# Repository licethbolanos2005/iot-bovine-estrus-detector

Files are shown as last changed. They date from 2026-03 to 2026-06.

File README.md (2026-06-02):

# 🐄 IoT Bovine Estrus Detector

Prototipo IoT basado en tecnología **LoRa** para la detección temprana del celo en bovinos mediante el monitoreo continuo de variables fisiológicas y comportamentales.

> Proyecto integrador — Ingeniería Electrónica  
> Unidad Central del Valle del Cauca - Semestre 8
> Autores: Liceth Bolaños, Santiago Albarracin, Arlyn Cardozo, Samuel Guevara

---

## 📋 Descripción general

El sistema integra un nodo transmisor montado en un chaleco portador adaptado al animal, el cual captura temperatura corporal, actividad motora, frecuencia respiratoria y eventos de monta. Los datos son procesados por un **ESP32 LoRa V3 (ESP32-S3 + SX1262)**, almacenados localmente en MicroSD con marca temporal RTC y transmitidos de forma inalámbrica al nodo receptor, donde son visualizados en **Grafana** a través de **InfluxDB**.

---

## 📁 Estructura del repositorio

```
iot-bovine-estrus-detector/
│
├── Board/                  # Diseño final de la PCB (KiCad)
│   └── ...                 # Archivos .kicad_pcb, .kicad_sch, Gerbers
│
├── Box/                    # Diseño de la caja de protección (impresión 3D)
│   └── ...                 # Archivos .ipt
│
├── Receiver_Code/          # Firmware del nodo receptor
│   └── ...                 # Código ESP32 — recepción LoRa, envío a InfluxDB
│
├── Schematic/              # Esquemático electrónico del sistema
│   └── ...                 # Archivos .kicad_sch
│
├── Transmitter_Code/       # Firmware del nodo transmisor
│   └── ...                 # Código ESP32 — sensores, LoRa, MicroSD, RTC, Web server
│
└── README.md
```

---

## ⚙️ Hardware utilizado

| Componente | Función |
|---|---|
| WiFi LoRa 32 V3 (ESP32-S3 + SX1262) | Unidad central de procesamiento y comunicación |
| DS18B20 | Medición de temperatura corporal |
| MPU6050 | Actividad motora y frecuencia respiratoria |
| FSR (Force Sensitive Resistor) | Detección de eventos de monta |
| INA219 | Monitoreo de consumo energético |
| DS3231 (RTC) | Registro temporal de datos |
| Módulo MicroSD TF | Almacenamiento local de datos |
| Batería LiPo 3.7V | Alimentación del sistema |

---

## 📡 Parámetros de comunicación LoRa

| Parámetro | Valor |
|---|---|
| Banda | 915 MHz (ISM) |
| Spreading Factor | 7 |
| Bandwidth | 125 kHz |
| Coding Rate | 5 |
| Sync Word | 0x12 |
| Potencia TX | 14 dBm |

---

## 🖥️ Arquitectura del sistema

```
[Sensores] → [ESP32 Transmisor] → [LoRa 915 MHz] → [ESP32 Receptor]
                    ↓                                        ↓
               [MicroSD + RTC]                        [InfluxDB → Grafana]
                    ↓
             [Servidor Web Embebido / OTA]
```

---

## 🚀 Primeros pasos

### Requisitos

- [Arduino IDE](https://www.arduino.cc/en/software) o [PlatformIO](https://platformio.org/)
- Placa: **Heltec WiFi LoRa 32 V3**
- Librerías necesarias:
  - `RadioLib`
  - `OneWire` + `DallasTemperature`
  - `MPU6050`
  - `RTClib`
  - `SD`
  - `INA219`
  - `ArduinoJson`
  - `ESPAsyncWebServer`

### Cargar firmware transmisor

1. Abre `Transmitter_Code/` en Arduino IDE o PlatformIO.
2. Configura los parámetros de red WiFi y LoRa en el archivo de configuración.
3. Compila y carga en la placa ESP32 del nodo transmisor.

### Cargar firmware receptor

1. Abre `Receiver_Code/` en Arduino IDE o PlatformIO.
2. Configura la dirección IP de InfluxDB y las credenciales de red.
3. Compila y carga en la placa ESP32 del nodo receptor.

---

## 📊 Visualización

Los datos son enviados a **InfluxDB** y visualizados en tiempo real mediante **Grafana**, donde se monitorean:

- Temperatura corporal (°C)
- Magnitud de aceleración (actividad motora)
- Frecuencia respiratoria
- Consumo energético (mA)
- Estado de celo (algoritmo de detección)
- Eventos de monta (FSR)
- Calidad del enlace LoRa (RSSI / SNR)

---

## 🌐 Servidor web embebido

El nodo transmisor implementa un servidor web accesible en la red local mediante:

```
http://boviot.local
```

Desde la interfaz web es posible:
- Visualizar variables fisiológicas en tiempo real
- Configurar parámetros de red WiFi
- Actualizar el firmware de forma inalámbrica (**OTA**)

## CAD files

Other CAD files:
Box/Caja PI/OldVersions/base.0005.ipt
Box/Caja PI/base.ipt
Box/Caja PI/tapa.ipt

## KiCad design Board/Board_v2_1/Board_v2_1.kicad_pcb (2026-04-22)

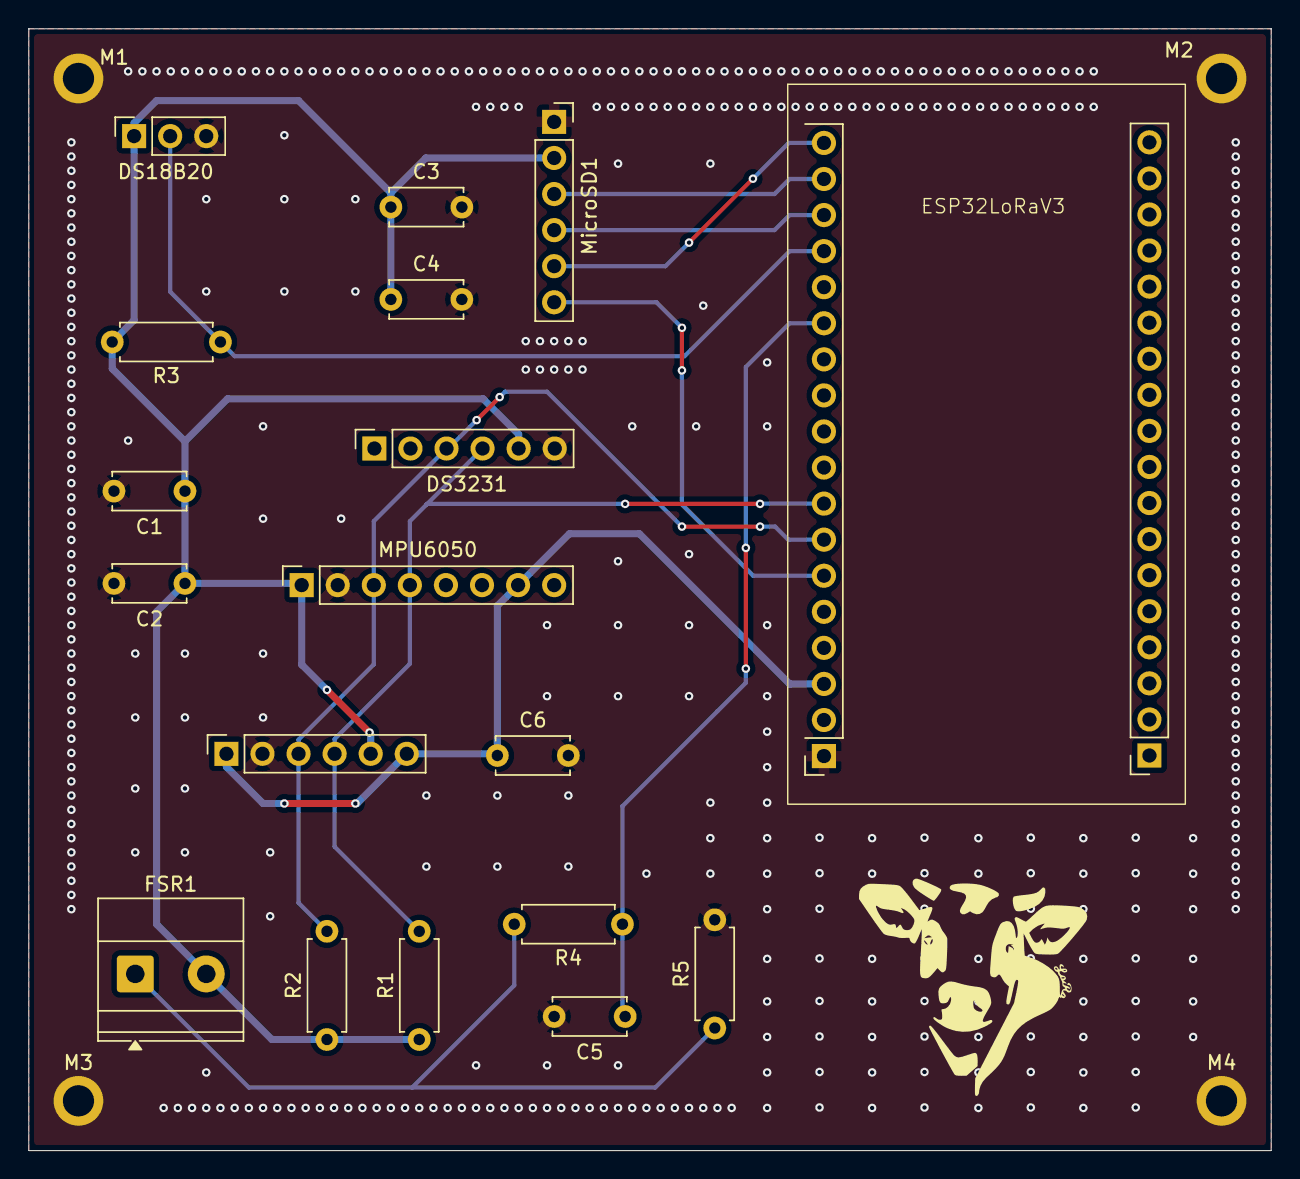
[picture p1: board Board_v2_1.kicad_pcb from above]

Board: 2 copper layers, 87.5 x 79.0 mm, 22 parts (0 on the bottom side), 12 nets.

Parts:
C1, C3, C5, C6: 100nf; C_Disc_D5.0mm_W2.5mm_P5.00mm
C2, C4: 10uf; C_Disc_D5.0mm_W2.5mm_P5.00mm
DS18B20: Conn_01x03; PinSocket_1x03_P2.54mm_Vertical
DS3231: PinSocket_1x06_P2.54mm_Vertical
ESP32LoRaV3: ESP32 Lora V3
FSR1: Conn_01x02; TerminalBlock_Phoenix_MKDS-1,5-2_1x02_P5.00mm_Horizontal
INA219: PinSocket_1x06_P2.54mm_Vertical
M1, M2, M3, M4: MountingHole_2.2mm_M2_ISO7380_Pad
MPU6050: Conn_01x08; PinSocket_1x08_P2.54mm_Vertical
MicroSD1: PinSocket_1x06_P2.54mm_Vertical
R1, R2, R3: 4.7K; R_Axial_DIN0207_L6.3mm_D2.5mm_P7.62mm_Horizontal
R4: 10K; R_Axial_DIN0207_L6.3mm_D2.5mm_P7.62mm_Horizontal
R5: 50K; R_Axial_DIN0207_L6.3mm_D2.5mm_P7.62mm_Horizontal

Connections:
+3V3: C6.1, ESP32LoRaV3.3 (3V3), INA219.1, INA219.6, MPU6050.7
/CS: ESP32LoRaV3.6 (GPIO45), MicroSD1.6
/FSR: C5.1, ESP32LoRaV3.13 (GPIO2), R4.1
/MISO: ESP32LoRaV3.17 (GPIO6), MicroSD1.3
/MOSI: ESP32LoRaV3.16 (GPIO5), MicroSD1.4
/SCK: ESP32LoRaV3.18 (GPIO7), MicroSD1.5
/SCL: DS3231.3, ESP32LoRaV3.7 (GPIO42), INA219.3, MPU6050.3, R2.2
/SDA: DS3231.4, ESP32LoRaV3.8 (GPIO41), INA219.4, MPU6050.4, R1.2
/TEMP: DS18B20.2, ESP32LoRaV3.15 (GPIO4), R3.1
GND: C1.2, C2.2, C3.2, C4.2, C5.2, C6.2, DS18B20.3, DS3231.6, ESP32LoRaV3.1 (GND), INA219.2, M1.1, M2.2, M3.2, M4.4, MPU6050.2, MicroSD1.1, R5.2
unnamed: FSR1.1, R4.2, R5.1
VIN-: C1.1, C2.1, C3.1, C4.1, DS18B20.1, DS3231.5, FSR1.2, INA219.5, MPU6050.1, MicroSD1.2, R1.1, R2.1, R3.2

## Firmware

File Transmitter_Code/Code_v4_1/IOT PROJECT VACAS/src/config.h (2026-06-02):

#ifndef CONFIG_H
#define CONFIG_H

#define FORZAR_RECALIBRACION_RTC  0

// ─── Pines I2C externos ───────────────────────────────
#define PIN_I2C_SDA         41
#define PIN_I2C_SCL         42

// ─── Pin 1-Wire DS18B20 ───────────────────────────────
#define PIN_ONE_WIRE        4
#define DS18B20_DESCONECTADO -127.0f

// ─── Pin ADC FSR ─────────────────────────────────────
#define PIN_FSR_ADC         2

// ─── Pines SPI SD Card ───────────────────────────────
#define PIN_SPI_MOSI        5
#define PIN_SPI_MISO        6
#define PIN_SPI_SCK         7
#define PIN_SD_CS           45

// ─── Pines LoRa SX1262 internos ──────────────────────
#define LORA_SCK            9
#define LORA_MOSI           10
#define LORA_MISO           11
#define LORA_CS             8
#define LORA_RST            12
#define LORA_IRQ            14
#define LORA_BUSY           13

// ─── Parámetros LoRa ─────────────────────────────────
#define LORA_FREQ           915.0
#define LORA_BW             125.0
#define LORA_SF             7
#define LORA_CR             5
#define LORA_SW             0x12
#define LORA_PWR            14
#define LORA_PREAMBLE       8

// ─── OLED interno ────────────────────────────────────
#define OLED_SDA            17
#define OLED_SCL            18
#define OLED_RST            21

// ─── Configuración general ───────────────────────────
#define SERIAL_BAUD         115200
#define DEVICE_ID           "collar_001"

// ─── Tiempos de las tasks (ms) ───────────────────────
#define INTERVALO_SENSORES  5000
#define INTERVALO_LORA      5000
#define INTERVALO_SD        10000

// ─── Tamaño queues FreeRTOS ──────────────────────────
#define QUEUE_DATOS_SIZE    5
#define QUEUE_ALERTAS_SIZE  5

// ─── Direcciones I2C ─────────────────────────────────
#define INA219_ADDR         0x40
#define MPU6050_ADDR        0x69

// ─── Umbrales detección celo ─────────────────────────
#define UMBRAL_ACTIVIDAD_ALTA   12.0f
#define UMBRAL_ACTIVIDAD_MEDIA  10.5f
#define UMBRAL_TEMP_ELEVADA     39.5f
#define UMBRAL_FSR_MONTA        2.0f
#define CICLOS_ACTIVIDAD_ALERTA 3

// ─── WiFi para OTA ────────────────────────────────────
#define WIFI_SSID       "PARRA CARDONA"
#define WIFI_PASSWORD   "JuanParra2005"
#define OTA_HOSTNAME    "collar_bovino_001"
#define OTA_PASSWORD    "ota_secret_123"

#endif // CONFIG_H

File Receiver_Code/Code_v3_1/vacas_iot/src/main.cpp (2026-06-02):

#include <Arduino.h>
#include <RadioLib.h>
#include <ArduinoJson.h>
#include <Wire.h>
#include "SSD1306Wire.h"
#include "config.h"
#include "wifi_manager.h"
#include "web_server.h"

// ─── Umbral FSR para evento de monta ───────────────────────────────────────
#define UMBRAL_FSR_MONTA  2.0f

// ─── OLED (pines internos Heltec V3) ───────────────────────────────────────
#define OLED_SDA  17
#define OLED_SCL  18
#define OLED_RST  21
SSD1306Wire display(0x3C, OLED_SDA, OLED_SCL);

// ─── Pines SX1262 internos del Heltec V3 ───────────────────────────────────
#define LORA_CS    8
#define LORA_IRQ   14
#define LORA_RST   12
#define LORA_BUSY  13

SX1262 radio = new Module(LORA_CS, LORA_IRQ, LORA_RST, LORA_BUSY);

volatile bool receivedFlag = false;

void IRAM_ATTR onReceive() {
  receivedFlag = true;
}

// ─── Mapeo nivel de celo ────────────────────────────────────────────────────
const char* nivelCeloStr(int n) {
  switch (n) {
    case 0: return "No detectado";
    case 1: return "Posible";
    case 2: return "Probable";
    case 3: return "Confirmado";
    default: return "Desconocido";
  }
}

const char* nivelCeloCorto(int n) {
  switch (n) {
    case 0: return "NO";
    case 1: return "POSIBLE";
    case 2: return "PROBABLE";
    case 3: return "CONFIRM.";
    default: return "?";
  }
}

// ─── OLED: pantalla de espera ───────────────────────────────────────────────
void mostrarEsperando() {
  display.clear();
  display.setFont(ArialMT_Plain_10);
  display.drawString(0, 0,  "  GATEWAY LoRa V3");
  display.drawString(0, 16, "─────────────────");
  display.drawString(0, 30, "  Esperando datos");
  display.drawString(0, 44, "  del nodo...");
  display.display();
}

// ─── OLED: datos del nodo ───────────────────────────────────────────────────
void mostrarDatos(float temp, const char* celo_corto, float consumo,
                  float fsr, bool monta, float rssi) {
  display.clear();
  display.setFont(ArialMT_Plain_10);
  display.drawString(0, 0,  "GATEWAY V3   " + String(rssi, 0) + "dBm");
  display.drawString(0, 11, "─────────────────────");
  display.drawString(0, 22, "T:" + String(temp, 1) + "C  " +
                            "I:" + String(consumo, 1) + "mA");
  display.drawString(0, 33, "FSR:" + String(fsr, 2) + "V  " +
                            "Monta:" + String(monta ? "SI" : "no"));
  display.drawString(0, 44, "Celo: " + String(celo_corto));
  display.display();
}

// ─── OLED: pantalla de inicio con IP ───────────────────────────────────────
void mostrarInicio(String ip, bool connected) {
  display.clear();
  display.setFont(ArialMT_Plain_10);
  display.drawString(0, 0,  "  GATEWAY LoRa V3");
  display.drawString(0, 12, "─────────────────");
  display.drawString(0, 24, connected ? "WiFi: Conectado" : "WiFi: Solo AP");
  display.drawString(0, 36, "IP: " + ip);
  display.drawString(0, 48, "LoRa: Escuchando");
  display.display();
}

// ─── Setup ──────────────────────────────────────────────────────────────────
void setup() {
  Serial.begin(115200);
  delay(1000);

  // Inicializar OLED
  pinMode(OLED_RST, OUTPUT);
  digitalWrite(OLED_RST, LOW);
  delay(50);
  digitalWrite(OLED_RST, HIGH);
  Wire.begin(OLED_SDA, OLED_SCL);
  display.init();
  display.flipScreenVertically();
  display.setFont(ArialMT_Plain_10);
  display.clear();
  display.drawString(0, 0,  "  GATEWAY LoRa V3");
  display.drawString(0, 16, "  Iniciando...");
  display.display();

  // Inicializar SPIFFS
  if (!initSPIFFS()) {
    Serial.println("[ERROR] SPIFFS no disponible");
  }

  // Cargar configuración
  String cfg = readConfig();
  Serial.println("[DEBUG] Config leída:");
  Serial.println(cfg);
  if (cfg == "") {
    Serial.println("[CONFIG] No existe config.json — usando por defecto");
    cfg = getDefaultConfig();
    saveConfig(cfg);
  }
  Serial.println("[CONFIG] OK");

  // Iniciar WiFi
  bool connected = startWifi(cfg);
  String ip = getIP();
  Serial.println("[WEB] Accede en: http://" + ip);

  // Iniciar Web Server
  startWebServer();

  // Mostrar IP en OLED
  mostrarInicio(ip, connected);
  delay(2000);

  // Inicializar LoRa
  Serial.println("[GATEWAY] Iniciando receptor LoRa...");
  int state = radio.begin(915.0, 125.0, 7, 5, 0x12, 14, 8);

  if (state != RADIOLIB_ERR_NONE) {
    Serial.print("[ERROR] Fallo al iniciar radio: ");
    Serial.println(state);
    display.clear();
    display.drawString(0, 20, "ERROR radio:");
    display.drawString(0, 35, "codigo: " + String(state));
    display.display();
    while (true);
  }

  Serial.println("[GATEWAY] Radio OK. Escuchando...");
  radio.setPacketReceivedAction(onReceive);

  state = radio.startReceive();
  if (state != RADIOLIB_ERR_NONE) {
    Serial.print("[ERROR] Fallo recepcion: ");
    Serial.println(state);
    while (true);
  }

  mostrarEsperando();
  Serial.println("[GATEWAY] Sistema listo");
}

// ─── Loop ───────────────────────────────────────────────────────────────────
void loop() {
  // Atender peticiones HTTP — debe llamarse siempre
  handleWebServer();

  // Procesar paquetes LoRa
  if (!receivedFlag) return;
  receivedFlag = false;

  String payload = "";
  int state = radio.readData(payload);

  if (state == RADIOLIB_ERR_NONE) {
    float rssi = radio.getRSSI();
    float snr  = radio.getSNR();

    Serial.println("─────────────────────────────────");
    Serial.print("[GATEWAY] RSSI : "); Serial.print(rssi); Serial.println(" dBm");
    Serial.print("[GATEWAY] SNR  : "); Serial.print(snr);  Serial.println(" dB");
    Serial.print("[GATEWAY] Bytes: "); Serial.println(payload.length());
    Serial.println("[GATEWAY] JSON recibido:");
    Serial.println(payload);

    // Guardar RSSI y SNR para el bridge
    Serial.print("[META] RSSI:"); Serial.print(rssi); Serial.println();
    Serial.print("[META] SNR:");  Serial.print(snr);  Serial.println();

    JsonDocument doc;
    DeserializationError error = deserializeJson(doc, payload);

    if (error) {
      Serial.print("[ERROR] JSON invalido: ");
      Serial.println(error.c_str());
      display.clear();
      display.drawString(0, 20, "JSON invalido");
      display.drawString(0, 35, "RSSI: " + String(rssi, 1));
      display.display();

    } else {
      const char* device_id  = doc["id"];
      int   rpm              = doc["s"]["rpm"];
      float temperatura      = doc["s"]["t"];
      float consumo_mA       = doc["s"]["mA"];
      float voltaje_V        = doc["s"]["V"];
      float fsr_voltaje      = doc["s"]["fsr"];
      int   nivel_num        = doc["c"]["n"];
      float actividad        = doc["c"]["act"];
      bool  monta            = doc["c"]["m"];
      const char* nivel_celo = nivelCeloStr(nivel_num);

      bool monta_calc = fsr_voltaje >= UMBRAL_FSR_MONTA;

      Serial.println("[OK] ─── Datos recibidos ───");
      Serial.print("[OK] Device   : "); Serial.println(device_id);
      Serial.print("[OK] Temp     : "); Serial.print(temperatura); Serial.println(" C");
      Serial.print("[OK] Accel    : "); Serial.print(actividad);   Serial.println(" m/s2");
      Serial.print("[OK] Celo     : "); Serial.println(nivel_celo);
      Serial.print("[OK] Consumo  : "); Serial.print(consumo_mA);  Serial.println(" mA");
      Serial.print("[OK] Voltaje  : "); Serial.print(voltaje_V);   Serial.println(" V");
      Serial.print("[OK] FSR      : "); Serial.print(fsr_voltaje); Serial.println(" V");
      Serial.print("[OK] Monta    : "); Serial.println(monta || monta_calc ? "SI" : "no");
      Serial.print("[OK] RPM      : "); Serial.print(rpm); Serial.println(" resp/min");

      mostrarDatos(temperatura, nivelCeloCorto(nivel_num),
                   consumo_mA, fsr_voltaje, monta || monta_calc, rssi);
    }

  } else if (state == RADIOLIB_ERR_CRC_MISMATCH) {
    Serial.println("[ERROR] CRC invalido — paquete corrupto");
  } else {
    Serial.print("[ERROR] Fallo lectura: ");
    Serial.println(state);
  }

  radio.startReceive();
}

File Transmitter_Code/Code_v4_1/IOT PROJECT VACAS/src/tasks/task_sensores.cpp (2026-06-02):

#include "task_sensores.h"
#include "queues_globales.h"
#include "../config.h"
#include "../sensors/sensor_ds18b20.h"
#include "../sensors/sensor_mpu6050.h"
#include "../sensors/sensor_ina219.h"
#include "../sensors/sensor_ds3232.h"
#include "../sensors/sensor_fsr.h"
#include <math.h>

QueueHandle_t     queue_datos       = NULL;
QueueHandle_t     queue_alertas     = NULL;
SemaphoreHandle_t mutex_i2c         = NULL;
SemaphoreHandle_t mutex_datos       = NULL;
DatosNodo         datos_compartidos = {};

void task_sensores(void *pvParameters) {
    Serial.println("[TASK_SENSORES] Iniciada");

    DatosNodo datos;
    strncpy(datos.device_id, DEVICE_ID, sizeof(datos.device_id));

    datos.anio             = 0;
    datos.mes              = 0;
    datos.dia              = 0;
    datos.hora             = 0;
    datos.minuto           = 0;
    datos.segundo          = 0;
    datos.temperatura      = 0.0f;
    datos.accel_x          = 0.0f;
    datos.accel_y          = 0.0f;
    datos.accel_z          = 0.0f;
    datos.giro_x           = 0.0f;
    datos.giro_y           = 0.0f;
    datos.giro_z           = 0.0f;
    datos.magnitud_accel   = 0.0f;
    datos.voltaje_V        = 0.0f;
    datos.corriente_mA     = 0.0f;
    datos.potencia_mW      = 0.0f;
    datos.fsr_raw          = 0;
    datos.fsr_voltaje      = 0.0f;
    datos.nivel_celo       = CELO_NO_DETECTADO;
    datos.temp_alta        = false;
    datos.monta            = false;
    datos.ciclos_actividad = 0;
    datos.datos_validos    = false;
    datos.rpm = 0;

    for (;;) {
        datos.datos_validos = true;

        // ── DS18B20 — 1-Wire, sin mutex ──────────────
        float temp = ds18b20_leer_temperatura();
        datos.temperatura = (temp != DS18B20_DESCONECTADO) ? temp : 0.0f;

        // ── FSR — ADC, sin mutex ─────────────────────
        datos.fsr_raw     = fsr_leer_raw();
        datos.fsr_voltaje = fsr_leer_voltaje();

        // ── Bus I2C — protegido con mutex ────────────
        if (xSemaphoreTake(mutex_i2c, pdMS_TO_TICKS(1000)) == pdTRUE) {

            DatosRTC rtc;
            if (ds3232_leer(rtc)) {
                datos.anio    = rtc.anio;
                datos.mes     = rtc.mes;
                datos.dia     = rtc.dia;
                datos.hora    = rtc.hora;
                datos.minuto  = rtc.minuto;
                datos.segundo = rtc.segundo;
            }

            DatosMPU6050 mpu;
            if (mpu6050_leer(mpu)) {
                datos.accel_x = mpu.accel_x;
                datos.accel_y = mpu.accel_y;
                datos.accel_z = mpu.accel_z;
                datos.giro_x  = mpu.giro_x;
                datos.giro_y  = mpu.giro_y;
                datos.giro_z  = mpu.giro_z;
                datos.magnitud_accel = sqrt(
                    mpu.accel_x * mpu.accel_x +
                    mpu.accel_y * mpu.accel_y +
                    mpu.accel_z * mpu.accel_z
                );
            } else {
                Serial.println("[TASK_SENSORES] MPU fallo — reiniciando...");
                mpu6050_init();
                datos.accel_x        = 0.0f;
                datos.accel_y        = 0.0f;
                datos.accel_z        = 0.0f;
                datos.magnitud_accel = 0.0f;
                datos.datos_validos  = false;
            }

            DatosINA219 ina;
            if (ina219_leer(ina)) {
                datos.voltaje_V    = ina.voltaje_bus;
                datos.corriente_mA = ina.corriente_mA;
                datos.potencia_mW  = ina.potencia_mW;
            }

            xSemaphoreGive(mutex_i2c);
        } else {
            Serial.println("[TASK_SENSORES] No se pudo tomar mutex I2C");
        }

        // ── Actualizar struct compartida ─────────────
// ── Actualizar struct compartida ─────────────
// Preserva campos calculados por otras tasks (rpm, nivel_celo, etc)
        if (xSemaphoreTake(mutex_datos, pdMS_TO_TICKS(100)) == pdTRUE) {
            uint8_t   rpm_prev          = datos_compartidos.rpm;
            NivelCelo nivel_prev        = datos_compartidos.nivel_celo;
            bool      temp_alta_prev    = datos_compartidos.temp_alta;
            bool      monta_prev        = datos_compartidos.monta;
            uint8_t   ciclos_prev       = datos_compartidos.ciclos_actividad;

            datos_compartidos = datos;

            datos_compartidos.rpm              = rpm_prev;
            datos_compartidos.nivel_celo       = nivel_prev;
            datos_compartidos.temp_alta        = temp_alta_prev;
            datos_compartidos.monta            = monta_prev;
            datos_compartidos.ciclos_actividad = ciclos_prev;

            xSemaphoreGive(mutex_datos);
        }

        // ── Notificar al detector — xQueueOverwrite
        // nunca falla aunque la queue esté llena ──────
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

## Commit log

2026-03-22 Primer esquemático del sistema IoT propuesto
    Primer esquemático del sistema IoT propuesto
    [Schematic_v1_1.kicad_sch]
2026-04-07 Corregí el bloque del acelerómetro
    Corregí el bloque del acelerómetro
    [Schematic_v1_2.kicad_pcb, Schematic_v1_2.kicad_sch]
2026-04-07 Code_v1_2
    Código con la corrección del acelerómetro agregado
2026-04-14 Modifiqué el esquemático de acuerdo a los nuevos cambios con el módulo ESP32 LoRa V3. Hice primer avance de pcb
    [Board_v1_1.kicad_pcb, Board_v1_1.kicad_sch]
2026-04-18 Se añadieron los planos de tierra y se realizaron vias stitching
    [Board_v2_1.kicad_pcb, Board_v2_1.kicad_sch]
2026-04-20 Se sube el código con la última actualización donde se cambia la esp32 y el módulo Ra-02 por 2 HiLetgo ESP32 V3 LoRa V3 SX1262
2026-04-22 Versión final de pcb
    [Board_v2_1.kicad_pcb]
2026-05-13 Se agrega el diseño de la caja para la PCB del nodo sensor
    [base.0005.ipt, base.ipt, tapa.ipt]
2026-05-23 Añadí primera versión del código del receptor, funcionando correctamente la recepción de datos
2026-05-23 Agregué versión completa del código del transmisor, con los sensores funcionando correctamente
2026-05-23 Se integró un web server para el receptor
2026-05-23 Se integró un web server para el transmisor
2026-05-23 Se agregó la variable de frecuencia respiratoria
2026-06-02 Se agregan versiones finales de código de receptor y código de transmisor
